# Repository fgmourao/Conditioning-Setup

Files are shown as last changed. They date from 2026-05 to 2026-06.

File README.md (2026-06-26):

<p align="left">
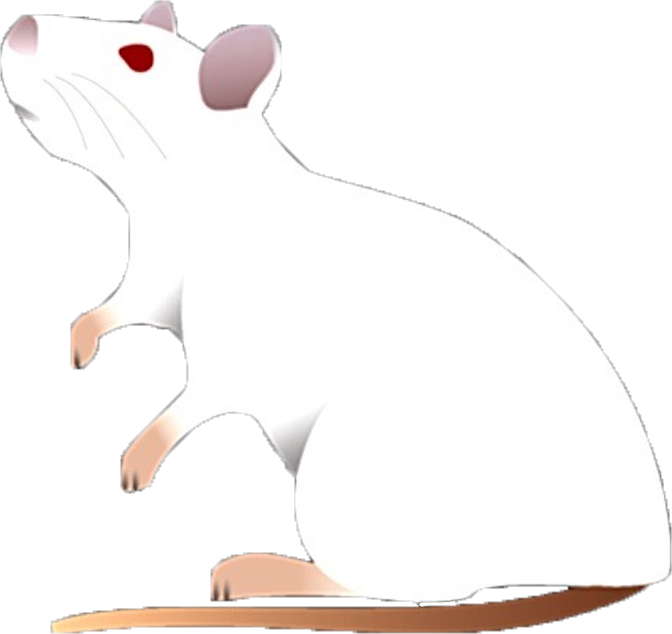
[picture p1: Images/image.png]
  
</p>

# Conditioning Setup v2.0
** Under development

Hardware, firmware and desktop interface for classical fear conditioning.
Arduino DUE stimulus generator controlled by a Python/PyQt5 application over USB.

---

## Origin

This project is a full rewrite of the system described in:

> Amaral Junior PA, Mourao FAG, Moraes MFD (2019).
> *A Custom Microcontrolled and Wireless-Operated Chamber for Auditory Fear Conditioning.*
> Frontiers in Neuroscience.
> https://doi.org/10.3389/fnins.2019.01193

The original v1.0 architecture used an ESP8266 as a Wi-Fi master communicating with the Arduino DUE via SPI, with a browser-based HTML interface. Version 2.0 removes the ESP8266 entirely — a PyQt5 desktop application communicates directly with the DUE over its native USB port.

Beyond the architectural change, v2.0 introduces several new capabilities: adaptive DAC lookup tables for lower harmonic distortion across the full frequency range, an AM modulation channel with configurable modulator frequency, two independent programmable digital trigger outputs (pins 10 and 11) for synchronising external equipment, an OLED status display, a hardware watchdog with fault detection, and a calibration interface with per-bar shock selection.

---

## Changes from v1.0 to v2.0

### Architecture
The ESP8266 Wi-Fi master and SPI bus are removed entirely. Python communicates directly with the DUE over its native USB port using newline-terminated JSON. All stimulus timing is handled autonomously by the DUE after a single `start` command — no real-time control from the host is required during execution.

### Bug fixes and stability improvements

**Shock clock decoupled from DAC** — in v1.0 the shock interval counter (`iCountShockIntervals`) was incremented inside the `carrier()` ISR, which ran at the DAC rate. Changing `carrier_freq` silently altered shock pulse timing. In v2.0 the shock has its own dedicated Timer6 running at a fixed 10 kHz, completely independent of the DAC.

**Hardware ABORT pin pullup** — in v1.0 `pinABORT` was configured as `INPUT` with no pullup resistor, leaving the pin floating when the button was not pressed and susceptible to spurious aborts from electrical noise. In v2.0 it uses `INPUT_PULLUP`.

**DAC disabled between sounds** — in v1.0 `analogWrite(DAC1, 0)` at sound offset wrote zero but left the DAC channel enabled, injecting DC noise into the amplifier between trials. In v2.0 `dacc_disable_channel` is called at every sound offset and the coupling capacitor is pre-charged to midscale before each onset to eliminate transients.

**Shock pulse timing precision** — in v1.0 `floor()` was used to convert pulse times to tick counts, introducing a systematic downward truncation error. In v2.0 `roundf()` gives the nearest tick (0.1 ms resolution at 10 kHz).

**Watchdog** — v1.0 had no hardware fault detection. If Timer4 or Timer6 stalled, the experiment continued silently with no stimuli. In v2.0 a software watchdog monitors both timers; if either stops incrementing for 5 seconds a fault is declared, all outputs are driven LOW, and the Python interface displays a critical alert.

**DAC buffer type** — in v1.0 the DAC buffer was `uint32_t` (4 bytes per sample), wasting twice the RAM needed. In v2.0 it is `uint16_t` (2 bytes per sample), halving the buffer footprint to 2 KB.

### Sound generation

In v1.0 the carrier lookup table had a fixed 8 samples regardless of frequency. At low carrier frequencies (1–3 kHz) this produced visible harmonic distortion — only 8 points approximated each sine cycle. In v2.0 adaptive tables select 4, 8, 16, or 32 samples based on the carrier frequency, keeping the DAC update rate within the optimal range across the full 0–20 kHz span.

### New stimuli and features

- **LIGHT** — independent light stimulus (pin 45, square wave or DC HIGH) with its own onset, duration, and frequency per trial
- **Trigger 1 / Trigger 2** — two independent digital pulse outputs (pins 10 and 11) for synchronising external equipment, with configurable onset (s) and duration (ms) per trial
- **Baseline period** — quiet time before the first trial, separate from the inter-trial interval
- **Per-trial volume control** — sound amplitude programmable per trial (0–100%)
- **AM modulation** — configurable modulator frequency per trial; `modulator_freq = 0` gives a pure sine
- **OLED status display** — real-time trial state on an SSD1306 128×32 display
- **Bar selection** — calibration mode allows fixing a single shock bar for individual verification
- **Python desktop interface** — replaces the ESP8266 HTML page with a PyQt5 application featuring a trial timeline preview, protocol save/load, event log, and calibration dialogs

---

## Architecture

```
Python / PyQt5  (PC)
      │
      │  SerialUSB — native USB port (USB CDC)
      │
Arduino DUE
      ├─ DAC1         →  Sound  (AM sine, 0–20 kHz)
      ├─ Timer4/5     →  DAC clock / AM modulator ISR
      ├─ Timer6       →  Shock clock (10 kHz)
      ├─ Timer7       →  Light square wave
      ├─ Pins 23–37   →  Shock bars (8 outputs, random sequence per trial)
      ├─ Pin 45       →  Light output
      ├─ Pin 46       →  Watchdog fault output
      ├─ Pin 48       →  Hardware ABORT input
      ├─ Pin 10        →  Trigger 1 output (digital pulse)
      ├─ Pin 11        →  Trigger 2 output (digital pulse)
      ├─ Pins 50–53   →  Sync outputs (SOUND, LIGHT, SHOCK, MOD)
      └─ Pins 20–21   →  I²C — OLED display (SDA / SCL)
```

The DUE stores the complete trial list in RAM and executes the experiment autonomously after a single `start` command. Python is responsible only for programming parameters, triggering execution, and monitoring status.

---

## Stimuli

Five independent stimuli with individual onset and duration per trial:

### Sound
- Output: DAC1 (12-bit, 0–3.3 V)
- Waveform: AM-modulated sine (`SINE_AM`) or pure sine
- Carrier: 0–20 kHz; modulator: 0–500 Hz
- Adaptive lookup tables (see [Sound generation](#sound-generation))
- AC coupling capacitor (10 µF) recommended in series on DAC1 output

### Light
- Output: pin 45, square wave 50% duty cycle
- Frequency: configurable; `light_freq = 9999` = DC HIGH (constant ON)

### Shock
- Outputs: pins 23, 25, 27, 29, 31, 33, 35, 37 (8 bars)
- Random sequence (Fisher-Yates shuffle) activation or fixed single bar (calibration)
- Pulse HIGH and LOW times configurable in ms (0.1 ms resolution at 10 kHz clock)

### Trigger 1 / Trigger 2
- Outputs: pin 10 (Trigger 1), pin 11 (Trigger 2)
- Simple digital HIGH pulse: onset in seconds, duration in milliseconds
- Independent of each other and of all other stimuli
- Intended for synchronising external equipment (cameras, stimulators, recording systems)

---

## Trial structure

Each trial stores 20 float parameters, transmitted semicolon-separated over serial:

| Field | Description | Unit |
|---|---|---|
| `baseline` | Quiet period before first trial | s |
| `silence` | Inter-trial interval | s |
| `onset_sound` | Sound onset within trial | s |
| `sound_duration` | Sound duration | s |
| `carrier_freq` | DAC carrier frequency; 0 = no sound | Hz |
| `modulator_freq` | AM modulator frequency; 0 = pure sine | Hz |
| `volume` | Sound amplitude | % |
| `waveform_type` | 0 = SINE_AM, 1 = SINE, 2 = SQUARE | — |
| `onset_shock` | Shock onset within trial | s |
| `shock_duration` | Shock duration; 0 = no shock | s |
| `pulse_high` | Shock bar ON time per pulse | ms |
| `pulse_low` | Shock bar OFF time between pulses | ms |
| `onset_light` | Light onset within trial | s |
| `light_duration` | Light duration; 0 = no light | s |
| `light_freq` | Light frequency; 9999 = DC HIGH | Hz |
| `bar_select` | 0 = Random sequence per trial, 1–8 = fixed bar, , 9 = sequential 1→8 (calibration "All") | — |
| `onset_trig1` | Trigger 1 onset within trial; 0 = start of trial | s |
| `trig1_duration` | Trigger 1 pulse duration; 0 = disabled | ms |
| `onset_trig2` | Trigger 2 onset within trial; 0 = start of trial | s |
| `trig2_duration` | Trigger 2 pulse duration; 0 = disabled | ms |

---

## Serial protocol

All communication uses newline-terminated JSON objects:

```
{"cmd":"ping"}
    -> {"ok":true,"msg":"pong","version":"2.0"}

{"cmd":"program","n":N,"data":"f0;f1;..."}
    -> {"ok":true,"msg":"N trials programmed"}

{"cmd":"start"}
    -> {"ok":true,"msg":"started"}

{"cmd":"abort"}
    -> {"ok":true,"msg":"aborted"}

{"cmd":"status"}
    -> {"ok":true,"status":N,"trial":N,"total":N,
        "running":bool,"ready":bool,"fault":bool}
```

Status codes: `0` IDLE · `1` READY · `2` RUNNING · `3` DONE · `4` FAULT · `5` ABORTED

---

## Sync outputs

All sync pins are active HIGH while the corresponding stimulus is active.
**Use these pins as the authoritative timing reference for external equipment** (electrophysiology, cameras). The `onset_*` fields in seconds carry a worst-case jitter of ~500 µs (one loop iteration); the sync pins do not.

| Pin | Signal | Description |
|---|---|---|
| 50 | SOUND_SYN | HIGH while sound is playing |
| 51 | LIGHT_SYN | HIGH while light is active |
| 52 | SHOCK_SYN | HIGH while shock is being delivered |
| 53 | MOD_SYN | Square wave at `modulator_freq`, phase-locked to AM envelope |

---

## OLED status display

Optional SSD1306 128×32 OLED on I²C (SDA = pin 20, SCL = pin 21, address 0x3C).
Shows experiment state at each transition:

| State | Display |
|---|---|
| Startup | `Conditioning Setup / Version 2.0` |
| Trial onset | `TRIAL X/N` / `CS` · `CS + US` · `US` |
| Done | `Conditioning Setup / Done` |
| Aborted | `Conditioning Setup / Aborted` |

The firmware runs normally if the display is not connected.

---

## Sound generation

v2.0 uses adaptive lookup tables (`Waveforms.h`) to minimise harmonic distortion across the full frequency range:

| Carrier frequency | Table size | DAC update rate |
|---|---|---|
| > 10 000 Hz | 4 samples | up to 80 kHz |
| > 3 000 Hz | 8 samples | up to 80 kHz |
| > 1 000 Hz | 16 samples | up to 48 kHz |
| ≤ 1 000 Hz | 32 samples | up to 32 kHz |

All rates are within the SAM3X8E DAC hardware limit of 1 MHz.
Buffer RAM cost: 32 × 32 × 2 bytes = 2 KB.

AM modulation uses a 32-sample unipolar envelope table. When `modulator_freq = 0` the carrier is output as a pure sine with no modulation.

---

## DAC signal conditioning

The DAC1 output is 0–3.3 V (unipolar, midscale = 1.65 V DC). A signal conditioning chain is required before the amplifier or speaker.

### Signal chain

```
DAC1 ── 10 µF (AC coupling) ── [ON-OFF-ON switch] ─┬─ Path A: direct output (external amplifier / measurement)
                                                  └─ Path B: Rs (12 kΩ) ── Rp (1 kΩ to GND)
                                                                     │
                                                                  POT (50 kΩ linear)
                                                                     │ cursor
                                                                  TDA8932 IN+
                                                                     │
                                                               OUT1 ── tweeter ── OUT2
```

### Components

| Component | Value | Purpose |
|---|---|---|
| C1 electrolytic | 10 µF, + toward DAC1 | Blocks 1.65 V DC offset; passes AC signal |
| Rs fixed resistor | 12 kΩ | Attenuates DAC signal to prevent amplifier saturation |
| Rp fixed resistor | 1 kΩ to GND | Anchors amplifier input when DAC is disabled; eliminates idle noise |
| Potentiometer | 50 kΩ linear | Volume control across full rotation range without clipping |
| TDA8932 module | Class-D, 12 V, BTL | Gain 30 dB (31.6×); differential output OUT1/OUT2 |
| Tweeter | 4 Ω, 40 W, 6–20 kHz | Connected differentially between OUT1 and OUT2 |

### ON-OFF-ON switch

A three-position toggle switch after the coupling capacitor selects the signal path:

| Position | Path | Use |
|---|---|---|
| ON (left) | Direct output after C1 | External amplifier, oscilloscope, audio interface |
| OFF (centre) | Mute | No signal at any output |
| ON (right) | Rs → Rp → POT → TDA8932 → tweeter | Normal experimental operation |

---

## Python application

### Requirements

```
pip install pyserial PyQt5
```

Python 3.8 or later.

### Features

- Dark/Light-theme PyQt5 desktop application
- Trial configuration panel: per-stimulus onset, duration, frequency, volume, pulse timing, trigger durations
- Recorded trials table with per-row delete
- Timeline preview: block diagram of all trials on a shared time axis with a real-time progress line during execution; rows are shown only for stimuli with non-zero duration
- Event log with timestamps (`YYYY-MM-DD HH:MM:SS`) — exportable via Save Log
- **Protocol menu:** Save Protocol, Load Protocol, Clear All Trials, Save Log
- **Calibration menu:** Sound, Light, Shock — continuous single-trial stimulus stopped by ABORT; shock calibration allows bar selection and configurable pulse timing
- **Help menu:** Info dialog
- Port selector with refresh button
- 4-second timeout warning if DUE does not respond after connection
- Firmware version check on connect (warns if not v2.0)
- Watchdog fault popup with critical alert
- Hardware ABORT button (pin 48) is read inside the trial timing loop and during inter-trial silences — responsive at any point during experiment execution

### Poll strategy

The poll timer (`{"cmd":"status"}` every 1500 ms) is stopped when the experiment starts to prevent USB interrupt collisions with Timer4 on the Native Port. One poll is scheduled at the calculated onset of each trial using `QTimer.singleShot`. A generation counter invalidates scheduled polls that remain pending after an ABORT. The poll timer resumes when the experiment ends or is aborted.

---

## Hardware requirements

| Component | Specification |
|---|---|
| Microcontroller | Arduino DUE |
| USB connection | Native port (second USB connector) |
| Shock bars | 8 outputs — pins 23, 25, 27, 29, 31, 33, 35, 37 |
| Light output | Pin 45 |
| Trigger 1 output | Pin 10 — digital pulse |
| Trigger 2 output | Pin 11 — digital pulse |
| ABORT button | Momentary switch — pin 48 to GND |
| DAC coupling | 10 µF electrolytic capacitor in series on DAC1 |
| Amplifier | Class-D module (e.g. TDA8932); 10–50 kΩ potentiometer at input |
| Speaker | Tweeter (2–20 kHz); 4 Ω or 8 Ω |
| OLED (optional) | SSD1306 128×32, I²C, address 0x3C |

---

## Files

| File | Description |
|---|---|
| `conditioning_setup_dark.py` | Main application — dark theme |
| `Stimuli_PY_DUE.ino` | Arduino DUE firmware |
| `Waveforms.h` | Adaptive DAC lookup tables |
| `image.png` | Logo displayed in the application header |

Arduino library dependencies (install via Arduino IDE Library Manager):
- **DueTimer** (Ivan Seidel)
- **Adafruit GFX Library**
- **Adafruit SSD1306**

---

## Desktop Executables

Pre-built executables are available for macOS and Windows. No Python installation is required — all dependencies are bundled inside the application package.

### macOS

**File:** `Conditioning Setup.app`

**Compatibility:** Built on Apple Silicon (M-series); runs natively on Apple Silicon Macs only.

**Installation:**
1. Download `Conditioning Setup.app`
2. Move it to your Applications folder or any preferred location
3. On first launch, macOS Gatekeeper may block the app because it is not signed by an Apple-registered developer. To allow it, open Terminal and run:

```bash
xattr -cr "/Applications/Conditioning Setup.app"
```

Then double-click the app to open normally.

**Build environment:**
- macOS 15.7.5 (Sequoia), Apple Silicon (M2)
- Python 3.12.2
- PyInstaller 6.x
- PyQt5 5.15.x, pyserial 3.x

**Build command:**
```bash
pyinstaller --windowed \
    --name "Conditioning Setup" \
    --icon "icon.icns" \
    --add-data "image.png:." \
    conditioning_setup_dark.py
```

---

### Windows

**File:** `Conditioning Setup.exe`

**Compatibility:** Windows 10 and Windows 11 (64-bit). Built on Windows 11; compatible with Windows 10 version 1903 or later.

**Installation:**
1. Download `Conditioning Setup.exe`
2. Place it in any folder
3. On first launch, Windows SmartScreen may display a warning ("Windows protected your PC"). Click **More info** → **Run anyway**. This warning appears because the executable is not digitally signed.

**USB driver:** the Arduino DUE native port uses a standard USB CDC driver. Windows 10 and 11 include this driver natively — no additional installation is required in most cases. If the COM port is not recognised, install the SAM-BA driver from the Arduino IDE or from the Microchip website.

**Build environment:**
- Windows 11, 64-bit
- Python 3.14.5
- PyInstaller 6.20.0
- PyQt5 5.15.x, pyserial 3.x

**Build command:**
```
py -m PyInstaller --onefile --windowed --name "Conditioning Setup" --icon "icon.ico" --add-data "image.png;." --add-data "icon.ico;." conditioning_setup_dark.py
```

---

## Known limitations

- Noise waveforms (white, pink) are not implemented. The lookup-table architecture is periodic; a possible approach is to generate noise buffers in Python (NumPy/SciPy) and send them as custom tables over serial.
- If the USB cable is disconnected during an experiment, the DUE continues executing autonomously. The only way to stop it is the hardware ABORT button (pin 48).

---

## License

Documentation licensed under Creative Commons Attribution-NonCommercial 4.0 International (CC BY-NC 4.0).

---

## Authors

**v1.0 (2019)**
Paulo Aparecido Amaral Junior, Flavio Afonso Goncalves Mourao, Marcio Flavio Dutra Moraes
*Núcleo de Neurociências, Federal University of Minas Gerais, Brazil*

**v2.0 (2026)**
Flavio Afonso Goncalves Mourao — [mourao.fg@gmail.com](mailto:mourao.fg@gmail.com)
*CNPq/MCTI/FNDCT Nº 21/2024 — Processo 446467/2024-3*
*Federal University of Minas Gerais, Brazil*

---

*Last update: June 2026*

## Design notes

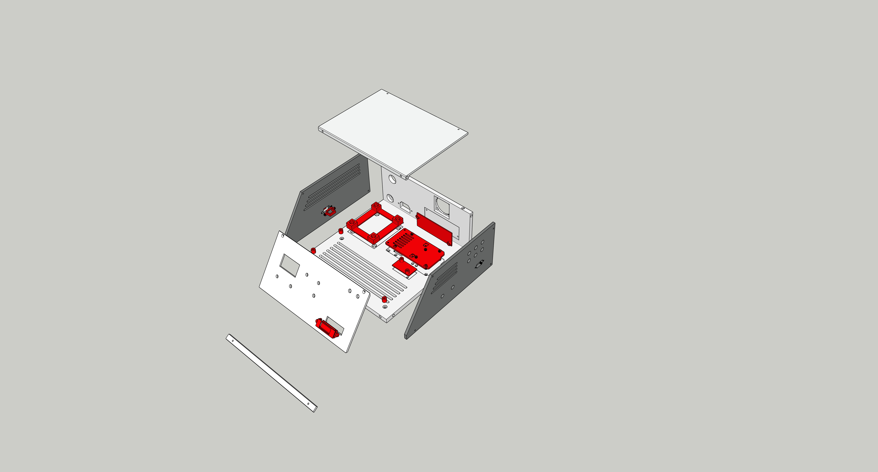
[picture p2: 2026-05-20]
3D_Cage/box_.jpg

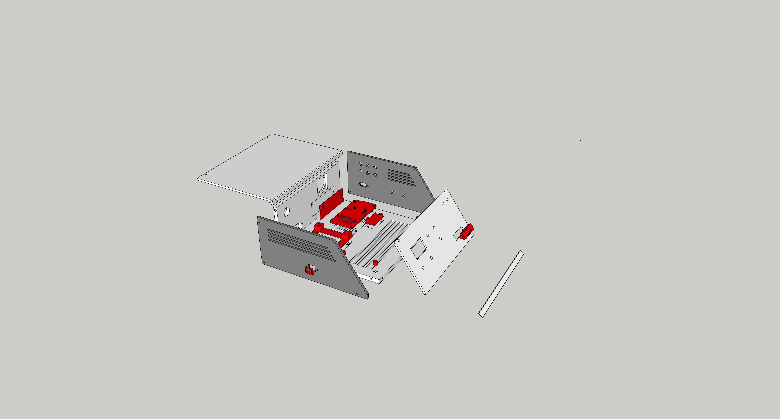
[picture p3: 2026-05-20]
3D_Cage/box_2.jpg

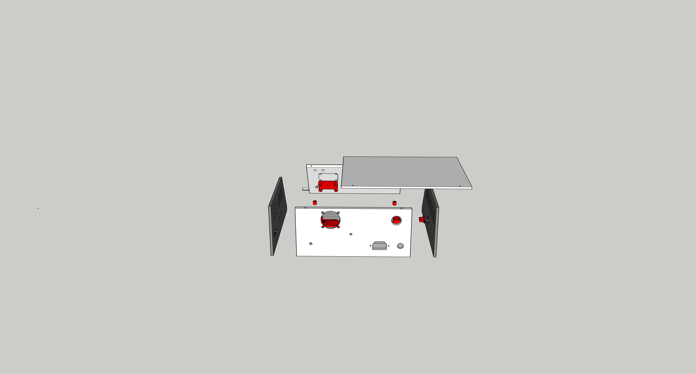
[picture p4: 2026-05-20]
3D_Cage/box_1.jpg

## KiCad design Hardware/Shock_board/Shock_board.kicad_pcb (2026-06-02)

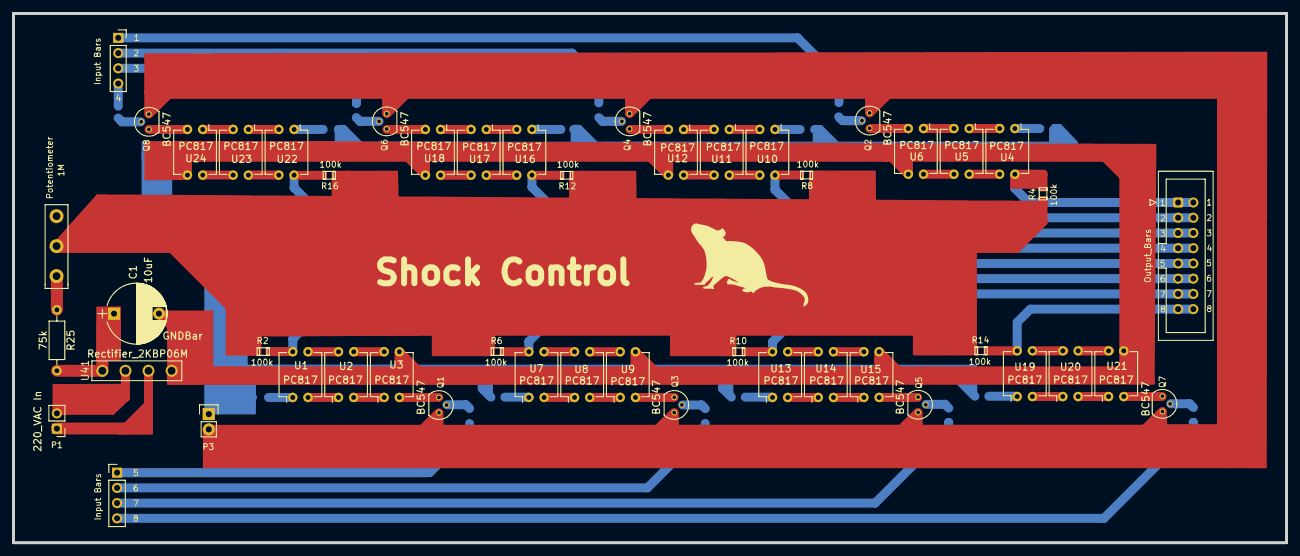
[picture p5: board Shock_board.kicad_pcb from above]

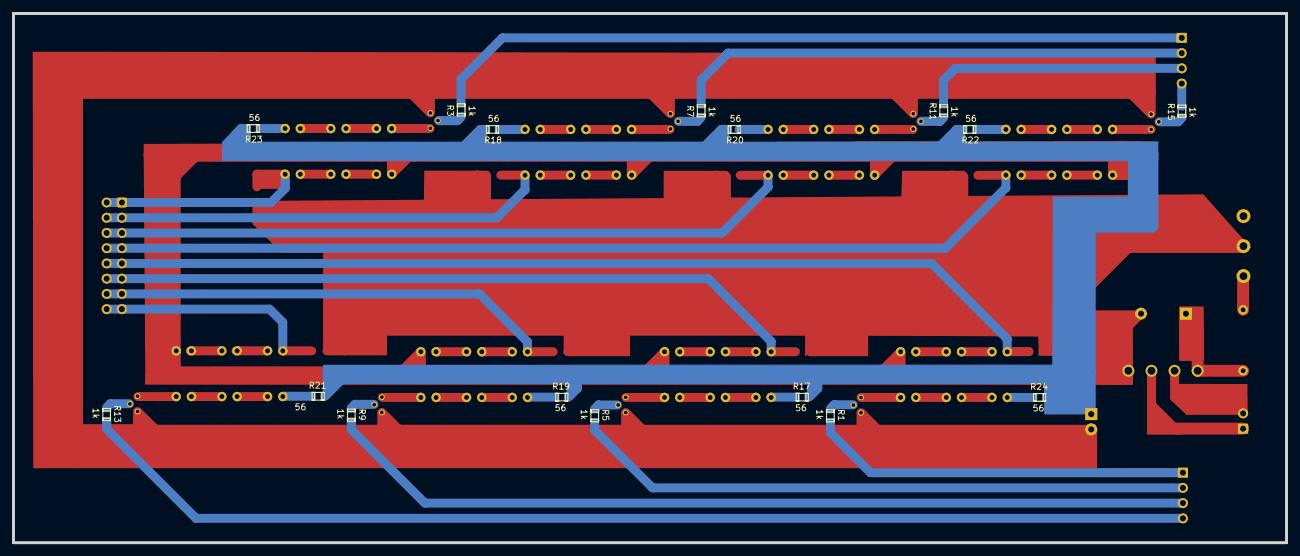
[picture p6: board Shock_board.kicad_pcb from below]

Board: 2 copper layers, 212.3 x 88.3 mm, 65 parts (16 on the bottom side), 80 nets.

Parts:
C1: 10uF; CP_Radial_D10.0mm_P7.50mm
Input Bars: PinHeader_1x04_P2.54mm_Vertical
Input Bars#2: PinSocket_1x04_P2.54mm_Vertical
Output_Bars: IDC-Header_2x08_P2.54mm_Vertical
P1: 220_VAC In; Pin_Header_Straight_1x02_Pitch2.54mm
P3: 5_VDC In; Pin_Header_Straight_1x02
Potentiometer: 1M; Potentiometer_Alps_RK163_Single_Vertical
Q1, Q2, Q3, Q4, Q5, Q6, Q7, Q8: BC547; TO-92_Molded_Narrow
R1, R3, R5, R7, R9, R11, R13, R15: 1k; SMD_0805
R2, R4, R6, R8, R10, R12, R14, R16: 100k; SMD_0805
R17, R18, R19, R20, R21, R22, R23, R24: 56; SMD_0805
R25: 75k; R_Axial_DIN0207_L6.3mm_D2.5mm_P10.16mm_Horizontal
U1, U2, U3, U4, U5, U6, U7, U8, U9, U10, U11, U12, U13, U14, U15, U16, U17, U18, U19, U20, U21, U22, U23, U24: PC817; DIP-4_W7.62mm
U41: Rectifier_2KBP06M

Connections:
5V_Arduino: P3.1, R17.2, R18.2, R19.2, R20.2, R21.2, R22.2, R23.2, R24.2
/InBarra1: Input Bars.1, R1.2
/InBarra2: Input Bars#2.1, R3.2
/InBarra3: Input Bars.2, R5.2
/InBarra4: Input Bars#2.2, R7.2
/InBarra5: Input Bars.3, R9.2
/InBarra6: Input Bars#2.3, R11.2
/InBarra7: Input Bars.4, R13.2
/InBarra8: Input Bars#2.4, R15.2
/OutBarra1: Output_Bars.9, Output_Bars.10, R2.2, U1.4
/OutBarra2: Output_Bars.1, Output_Bars.2, R4.2, U4.4
/OutBarra3: Output_Bars.11, Output_Bars.12, R6.2, U7.4
/OutBarra4: Output_Bars.3, Output_Bars.4, R8.2, U10.4
/OutBarra5: Output_Bars.13, Output_Bars.14, R10.2, U13.4
/OutBarra6: Output_Bars.5, Output_Bars.6, R12.2, U16.4
/OutBarra7: Output_Bars.15, Output_Bars.16, R14.2, U19.4
/OutBarra8: Output_Bars.7, Output_Bars.8, R16.2, U22.4
/Vtrafo+: P1.1, U41.3
/Vtrafo-: P1.2, U41.2
GndArduino: P3.2, Q1.3 (E), Q2.3 (E), Q3.3 (E), Q4.3 (E), Q5.3 (E), Q6.3 (E), Q7.3 (E), Q8.3 (E)
GndBarra: C1.2, U3.3, U6.3, U9.3, U12.3, U15.3, U18.3, U21.3, U24.3, U41.4 (-)
unnamed: Q1.2 (B), R1.1
unnamed: Q1.1 (C), U3.2
unnamed: Q2.2 (B), R3.1
unnamed: Q2.1 (C), U6.2
unnamed: Q3.2 (B), R5.1
unnamed: Q3.1 (C), U9.2
unnamed: Q4.2 (B), R7.1
unnamed: Q4.1 (C), U12.2
unnamed: Q5.2 (B), R9.1
unnamed: Q5.1 (C), U15.2
unnamed: Q6.2 (B), R11.1
unnamed: Q6.1 (C), U18.2
unnamed: Q7.2 (B), R13.1
unnamed: Q7.1 (C), U21.2
unnamed: Q8.2 (B), R15.1
unnamed: Q8.1 (C), U24.2
unnamed: R17.1, U7.1
unnamed: R18.1, U10.1
unnamed: R19.1, U13.1
unnamed: R20.1, U16.1
unnamed: R21.1, U19.1
unnamed: R22.1, U22.1
unnamed: R23.1, U4.1
unnamed: R24.1, U1.1
unnamed: Potentiometer.3, R25.1
unnamed: U1.2, U2.1
unnamed: U1.3, U2.4
unnamed: U2.2, U3.1
unnamed: U2.3, U3.4
unnamed: U4.2, U5.1
unnamed: U4.3, U5.4
unnamed: U5.2, U6.1
unnamed: U5.3, U6.4
unnamed: U7.2, U8.1
unnamed: U7.3, U8.4
unnamed: U8.2, U9.1
unnamed: U8.3, U9.4
unnamed: U10.2, U11.1
unnamed: U10.3, U11.4
unnamed: U11.2, U12.1
unnamed: U11.3, U12.4
unnamed: U13.2, U14.1
unnamed: U13.3, U14.4
unnamed: U14.2, U15.1
unnamed: U14.3, U15.4
unnamed: U16.2, U17.1
unnamed: U16.3, U17.4
unnamed: U17.2, U18.1
unnamed: U17.3, U18.4
unnamed: U19.2, U20.1
unnamed: U19.3, U20.4
unnamed: U20.2, U21.1
unnamed: U20.3, U21.4
unnamed: U22.2, U23.1
unnamed: U22.3, U23.4
unnamed: U23.2, U24.1
unnamed: U23.3, U24.4
unnamed: C1.1, R25.2, U41.1 (+)
Vbarra: Potentiometer.2, R2.1, R4.1, R6.1, R8.1, R10.1, R12.1, R14.1, R16.1

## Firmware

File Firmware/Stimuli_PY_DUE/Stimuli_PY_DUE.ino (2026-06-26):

/* Stimuli_PY_DUE.ino
 *
 * PROJECT : Conditioning Setup
 * Arduino DUE stimulus generator for classical fear conditioning.
 * Version: 2.0
 *
 * Architecture:
 *   Controlled entirely via the SerialUSB native port (Python on PC).
 *   Note: SerialUSB.begin(115200) is called for completeness but the baudrate
 *   parameter is ignored on the Native Port -- USB CDC always runs at USB speed.
 *   The DUE stores the complete trial list in RAM and executes the experiment
 *   autonomously after receiving a START command. Python manages timing only
 *   at the experiment level (sending parameters and start/abort); all stimulus
 *   onset/offset timing is handled by the DUE using micros() at 500 us resolution.
 *
 * Sound generation (Waveforms.h adaptive lookup tables):
 *   carrier_freq >  10000 Hz:  4-sample table  (DAC Timer4 rate up to  80 kHz)
 *   carrier_freq >   3000 Hz:  8-sample table  (DAC Timer4 rate up to  80 kHz)
 *   carrier_freq >   1000 Hz: 16-sample table  (DAC Timer4 rate up to  48 kHz)
 *   carrier_freq <=  1000 Hz: 32-sample table  (DAC Timer4 rate up to  32 kHz)
 *   All rates are within the SAM3X8E DAC hardware limit of 1 MHz.
 *   Modulator: fixed 32-sample unipolar [0,1] table. Timer5 rate = modulator_freq x 32.
 *   modulator_freq = 0: pure carrier sine, no AM modulation.
 *   Waveform types: SINE_AM (0), SINE (1), SQUARE (2).
 *                   NOTE (v2.0): SINE and SQUARE are implemented in firmware but currently
 *                   unused. The Python UI always sends waveform_type=0 (SINE_AM), which
 *                   falls back to pure sine when modulator_freq=0. SINE/SQUARE remain
 *                   available via manual protocol edit and may be re-enabled in a future UI release. 
 * Five independent stimuli with individual onset/offset timing:
 *   SOUND    -- DAC1, AM sine or pure sine or square wave, Timer4/Timer5
 *   SHOCK    -- 8 bar pins random sequence (Fisher-Yates shuffle), Timer6 at 10 kHz clock
 *   LIGHT    -- pin 45, square wave 50% duty cycle, Timer7
 *   TRIGGER1 -- pin 10, digital HIGH pulse, duration in ms
 *   TRIGGER2 -- pin 11, digital HIGH pulse, duration in ms
 *
 * OLED status display (128x32, SSD1306, I2C address 0x3C):
 *   Wired to DUE I2C bus: SDA = pin 20, SCL = pin 21.
 *   Shows experiment state at each transition:
 *     Startup  : "Conditioning Setup / Ready."
 *     Trial    : "TRIAL X/N / CS"  or  "CS + US"  or  "US"
 *     Done     : "Conditioning Setup / Done"
 *     Aborted  : "Conditioning Setup / Aborted"
 *   Updated in RunTrial() before ProgramSound() -- no audio glitch risk.
 *   sendStatus() is also called at the same point to notify Python of trial onset.
 *
 * SerialUSB protocol (newline-terminated JSON, USB CDC speed):
 *   {"cmd":"ping"}                              -> {"ok":true,"msg":"pong","version":"2.0"}
 *   {"cmd":"status"}                            -> {"ok":true,"status":N,"trial":N,...}
 *   {"cmd":"program","n":N,"data":"f0;f1;..."}  -> {"ok":true,"msg":"N trials programmed"}
 *   {"cmd":"start"}                             -> {"ok":true,"msg":"started"}
 *   {"cmd":"abort"}                             -> {"ok":true,"msg":"aborted"}
 *
 *   program data format: N x FIELDS_PER_TRIAL floats, semicolon-separated, row-major.
 *   Field order per trial: baseline, silence, onset_sound, sound_duration, carrier_freq,
 *   modulator_freq, volume, waveform_type, onset_shock, shock_duration, pulse_high,
 *   pulse_low, onset_light, light_duration, light_freq, bar_select,
 *   onset_trig1, trig1_duration, onset_trig2, trig2_duration.
 *
 * Sync outputs (all active HIGH while the corresponding stimulus is active):
 *   pin 50 -- SOUND_SYN  sound active
 *   pin 51 -- LIGHT_SYN  light active
 *   pin 52 -- SHOCK_SYN  shock active
 *   pin 53 -- MOD_SYN    square wave at modulator_freq (phase-locked to AM envelope)
 *
 *   TIMING REFERENCE: the sync pins are driven at the exact moment of stimulus
 *   onset/offset inside the RunTrial() timing loop. Use these pins as the
 *   timing reference for external equipment (electrophysiology,
 *   cameras, etc.). The onset_* fields in seconds have a worst-case jitter of
 *   ~500 us (one loop iteration) and ~250 us typical.
 *
 * Pin assignments:
 *   DAC1 -- sound output (12-bit, 0-3.3V)
 *   45   -- light stimulus output (square wave, 50% duty)
 *   46   -- watchdog fault output (HIGH pulse on fault)
 *   48   -- hardware ABORT input (INPUT_PULLUP, active LOW)
 *   13   -- debug LED (ON when parameters received OK, OFF after abort)
 *   20   -- I2C SDA (OLED display)
 *   21   -- I2C SCL (OLED display)
 *   10   -- Trigger 1 output (HIGH during trig1_duration ms after onset_trig1)
 *   11   -- Trigger 2 output (HIGH during trig2_duration ms after onset_trig2)
 *   23,25,27,29,31,33,35,37 -- shock bar outputs (active HIGH, random sequence per trial)
 *
 * Timer allocation:
 *   Timer4 -- carrier()    ISR: writes DACbuffer samples to DAC1
 *   Timer5 -- modulating() ISR: advances modulator index, drives MOD_SYN
 *   Timer6 -- shockClock() ISR: 10 kHz shock bar timing clock
 *   Timer7 -- lightClock() ISR: light square wave toggle
 *
 * Version 1.0 (2019): ESP8266 WiFi master + Arduino DUE SPI slave architecture.
 *   Authors: Paulo Aparecido Amaral Junior, Flavio Afonso Goncalves Mourao, Marcio Flavio Dutra Moraes
 *            Nucleo de Neurociencias UFMG/Brazil
 *            https://doi.org/10.3389/fnins.2019.01193
 *
 * Version 2.0 (2026)
 *   Author:  Flavio Afonso Goncalves Mourao  mourao.fg@gmail.com
              Federal University of Minas Gerais (UFMG) - Brazil

    Started:     12/2023
    Last update: 06/2026

 */

#include "DueTimer.h"
#include "Waveforms.h"
#include <Wire.h>
#include <Adafruit_GFX.h>
#include <Adafruit_SSD1306.h>

#define SCREEN_WIDTH  128
#define SCREEN_HEIGHT  32
Adafruit_SSD1306 display(SCREEN_WIDTH, SCREEN_HEIGHT, &Wire, -1);

/*############################################################################################################
        Constants
############################################################################################################*/

// Maximum number of trials stored in RAM.
// Increasing this also requires increasing sbuf (see sizing table below).
#define MAX_TRIALS          100

// Number of float fields per trial (must match Python FIELDS list).
#define FIELDS_PER_TRIAL    20

// SAM3X8E hardware DAC update rate limit: 1 MHz.
// Timer4 frequency = carrier_freq x nC must not exceed this value.
#define DAC_MAX_RATE        1000000.0f

// Timer6 runs at this fixed frequency to clock the shock bar state machine.
// Resolution: 1 / SHOCK_CLOCK_HZ = 0.1 ms per tick.
// pulse_high and pulse_low (ms) are converted to tick counts in ProgramShock().
#define SHOCK_CLOCK_HZ      10000.0f

// Watchdog: if Timer4 or Timer6 stops incrementing for this long, trigger a fault.
#define WATCHDOG_TIMEOUT_MS 5000UL

// Duration of the fault pulse on pinERROR (ms).
#define WATCHDOG_PULSE_MS   200UL

// Waveform type identifiers (stored as float in Trial struct, cast to int in ProgramSound).
// NOTE: SINE and SQUARE are functional but not exposed in the current Python UI.
// All trials from cage_app.py currently send waveform_type = WAVE_SINE_AM.
#define WAVE_SINE_AM  0  // AM-modulated sine: carrier amplitude follows modulator envelope
#define WAVE_SINE     1  // Pure sine: no AM, modulator table ignored (not used by UI)
#define WAVE_SQUARE   2  // Square wave: DAC alternates between 0 and 4095*vol (not used by UI)

// Experiment status codes returned in JSON status responses.
#define ST_IDLE    0  // Waiting for parameters
#define ST_READY   1  // Parameters received, ready to start
#define ST_RUNNING 2  // Experiment in progress
#define ST_DONE    3  // All trials completed normally
#define ST_FAULT   4  // Watchdog fault detected, experiment aborted
#define ST_ABORTED 5  // Aborted by Python command or hardware button

/*############################################################################################################
        Pin assignments
############################################################################################################*/

// Hardware ABORT button: INPUT_PULLUP, active LOW.
// Connects between pin 48 and GND. Triggers immediate Abort() when pressed.
static const int pinABORT      = 48;
// Sync outputs: driven HIGH at stimulus onset, LOW at offset.
// Used for external recording synchronisation (e.g. electrophysiology, camera trigger).
static const int pinSOUND_SYN  = 50;
static const int pinSHOCK_SYN  = 52;
static const int pinLIGHT_SYN  = 51;
// Modulator sync: square wave at modulator_freq, phase-locked to the AM envelope.
// Transitions at iM==0 (LOW) and iM==MOD_SAMPLES_WF/2 (HIGH) inside modulating() ISR.
// Useful for locking external equipment to the AM cycle.
static const int pinMOD_SYN    = 53;
// Light stimulus output: square wave at light_freq, 50% duty cycle, driven by Timer7.
static const int pinLIGHT      = 45;
// Watchdog fault indicator: HIGH pulse of WATCHDOG_PULSE_MS on timer fault.
static const int pinERROR      = 46;
// Debug Light: ON when trial parameters are loaded, OFF after Abort().
static const int pinLIGHT_DBG  = 13;

// Trigger outputs: driven HIGH at onset, LOW at offset.
// Independent programmable digital pulses for synchronising external equipment.
static const int pinTRIG1      = 10;
static const int pinTRIG2      = 11;

// Shock bar pins: 8 pins starting at iInitialBar, spaced by barStep.
// Round-robin activation: one bar active at a time, advancing each pulse cycle.
static const int iInitialBar   = 23;
static const int nBars         = 8;
static const int barStep       = 2;

// Shock bar pin array and random order buffer.
static int barPins[nBars]      = {23,25,27,29,31,33,35,37};
static int barOrder[nBars];
static int barOrderIdx         = 0;

/*############################################################################################################
        Trial structure
        Each field is stored as float for uniform SerialUSBisation.
        Times are in seconds; frequencies in Hz; volume in %; pulse times in ms.
############################################################################################################*/

struct Trial {
  float baseline;        // Baseline period before first trial starts (s)
  float silence;         // Inter-trial silence before this trial starts (s)
  float onset_sound;     // Sound onset time within trial (s), relative to trial start
  float sound_duration;  // Sound duration (s)
  float carrier_freq;    // DAC carrier frequency (Hz); 0 = no sound
  float modulator_freq;  // AM modulator frequency (Hz); 0 = pure sine
  float volume;          // Sound amplitude (%), 0-100
  float waveform_type;   // 0=SINE_AM, 1=SINE, 2=SQUARE (cast to int in ProgramSound). Python UI always sends 0; SINE/SQUARE reserved for future use.
  float onset_shock;     // Shock onset time within trial (s)
  float shock_duration;  // Shock duration (s); 0 = no shock
  float pulse_high;      // Shock bar ON time per pulse (ms)
  float pulse_low;       // Shock bar OFF time between pulses (ms)
  float onset_light;     // Light onset time within trial (s)
  float light_duration;  // Light duration (s); 0 = no light
  float light_freq;      // Light square wave frequency (Hz); 9999 = DC HIGH (constant ON)
  float bar_select;      // Shock bar selection: 0 = random sequence (experiment); 1-8 = fixed bar; 9 (sentinel) = sequential 1->8 (calibration "All")
  float onset_trig1;     // Trigger 1 onset time within trial (s)
  float trig1_duration;  // Trigger 1 pulse duration (ms); 0 = disabled
  float onset_trig2;     // Trigger 2 onset time within trial (s)
  float trig2_duration;  // Trigger 2 pulse duration (ms); 0 = disabled
};
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

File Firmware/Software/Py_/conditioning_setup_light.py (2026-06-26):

"""
conditioning_setup.py
===========
PROJECT : Conditioning Setup
VERSION : 2.0

DESCRIPTION:
    PyQt5 graphical interface for the Conditioning Setup Arduino DUE.
    The DUE runs Stimuli_PY_DUE.ino and controls five independent stimuli:
    - SOUND (DAC1, AM sine), 
    - LIGHT (pin 45, square wave 50% duty cycle),
    - SHOCK (8 bar pins,random sequence per trial), 
    - TRIGGER 1 (pin 10, digital pulse), 
    - TRIGGER 2 (pin 11, digital pulse). 
    
    This application programs trial parameters, triggers execution, and monitors status in real time.

SERIAL PROTOCOL (newline-terminated JSON, USB CDC speed):
    All commands are sent as compact JSON objects followed by newline.
    All responses from the DUE are also newline-terminated JSON objects.

    Commands sent by Python:
        {"cmd":"ping"}
            -> {"ok":true,"msg":"pong","version":"2.0"}
               Verifies that the DUE is alive and responsive.

        {"cmd":"program","n":N,"data":"f0;f1;..."}
            -> {"ok":true,"msg":"N trials programmed"}
               Sends N trials. 'data' is a flat semicolon-separated string of
               N x 20 float values in row-major order, matching FIELDS exactly.

        {"cmd":"start"}
            -> {"ok":true,"msg":"started"}
               Starts the experiment. RunExperiment() on the DUE is blocking;
               the DUE handles all stimulus timing autonomously after this.

        {"cmd":"abort"}
            -> {"ok":true,"msg":"aborted"}
               Immediately stops all stimuli and resets the DUE state machine.

        {"cmd":"status"}
            -> {"ok":true,"status":N,"trial":N,"total":N,
                "running":bool,"ready":bool,"fault":bool}
               Returns the current experiment state. Called automatically by
               the poll timer every 1500 ms while connected.

    DUE status codes:
        0 = IDLE     -- waiting for parameters
        1 = READY    -- parameters loaded, ready to start
        2 = RUNNING  -- experiment in progress
        3 = DONE     -- all trials completed normally
        4 = FAULT    -- watchdog fault, experiment aborted
        5 = ABORTED  -- aborted by command or hardware button
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
